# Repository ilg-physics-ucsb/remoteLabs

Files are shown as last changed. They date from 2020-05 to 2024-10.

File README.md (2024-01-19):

# UCSB Physics Remote Labs
This is the code base for remote-controlling apparatus used for laboratory instruction in modern physics labs.  It was created to serve our students who can't come onto campus during quarantine 2020.

## Installation and Setup

At the time of writing we are using the Raspbery Pi 4 (4GB model) with Raspbian Lite Buster installed. Raspbian Lite was chosen to minimize overhead on the CPU while still using a distro design for use with UV4L.

### Raspbian Lite

The simplest way to get Raspbian Lite is to go to the [Raspberry Pi downloads](https://www.raspberrypi.org/downloads/) page and follow one of the first three links to download the imager. Choose the link based on the operating system you are running on your own computer, not the Raspberry Pi.

Once you have the imager installed simply ask it to flash Raspbian Lite onto the SD Card. You do this by clicking the select OS button and then selection other Raspbian OS's. Then select Raspbian Lite 32-Bit. 

---
#### Making SSH work

Before you put the SD card in the Pi, you will need put an empty file named ssh in the root directory of the sd card. You can do this is terminal/command prompt.

In terminal `cd` to the SD card. On OSX that is usually under /Volumes/boot. On Linux I think it is in /mnt/boot (but I don't know for sure), then run the command

```bash
sudo touch ssh
```

On Windows open a command prompt and type `<letter>:` Replace <letter> by whatever capiatl letter windows assigned to the SD Card. (Typically D or E). Then run the command

```
echo "" > ssh
```

#### Making WiFi work

You are almost ready to plug in the SD Card.  The final step is to enable ``headless'' operation of the Pi (i.e., without its own keyboard/mouse/monitor) by giving the Pi access to your WiFi when it boots. To do that you need to add one more file to the root directory of the SD card.  This file must be named [wpa_supplicant.conf](https://www.raspberrypi.org/documentation/configuration/wireless/headless.md) 

On Windows, you can make the file in any simple text editor on your computer and then drag and drop it onto the SD card. On Mac, there can be issues when copying and pasting to a text editor and then moving it. It is best to type it out long form. The contents of the file should look like the following:
```bash
ctrl_interface=DIR=/var/run/wpa_supplicant GROUP=netdev
update_config=1
country=<Insert 2 letter ISO 3166-1 country code here>

network={
 ssid="<Name of your WiFi>"
 psk="<Password for your WiFi>"
}
```
Replacing the three entries between angle brackets < > with your information.

Now you can plug in your SD card into the Pi and boot. You should then be able to SSH into your Pi.

---
### SSH

#### Getting the IP Address
In order to connect to your Raspberry Pi, you will need to know its IP Address. To figure that out, typically log onto your router and look and the DHCP leases. How to do this varies from router to router, but it typically starts by opening a browser and typing "192.168.1.1" in the adress bar (without the quotes). If that doesn't work try "192.168.0.1" and if that doesn't work try "10.0.0.1". If none of those work try the following commands in terminal/command prompt/Powershell:

OSX/Linux
```bash
ifconfig
```

Windows
```
ipconfig \all
```
And look for somthing labeled "gateway" that should be the IP address of your router. Type that set of numbers into your browser's address bar.

Finally, if that doesn't work, google the make and model of your router.

To access your router's information typically requires a username and password. Most routers have a default that is written on the bottom of the router or available via google. If you haven't changed anything then that should be the log in information.

You will have to look around your router's website to find a list of connected devices and their IP addresses. One of them should be named "raspberrypi". Again it should look like 192.168.1.61 or something similar. (Note: you want the IPV4 address not the IPV6.)

---
#### Getting into the Pi

To SSH into your Pi use Terminal or Powershell *(not command prompt)*. Simply type the command

```bash
ssh pi@<ip_address>
```

Replacing <ip_address> with the address you found one your router's website. (Note: Make sure your Pi has been on for about a minute before you try this command.  It won't work if the Pi is still booting up.)

You will be asked for a password. The default password for raspberry pi's is the word "raspberry" without the quotes.

The terminal should then look somthing like 
```
pi@raspberrypi:~$
```
If everything went seccussfully.

---
### Configuring the Pi
Now run the command
```bash
sudo raspi-config
```
This will open a colorful window that you can navigate using the tab, enter and arrow keys.

Start by changing your password to something that you will remember. (Just press Enter on your keyboard.)

Then arrow down to "5 Interfacing Options"

You will want to do a few things in that window, but be aware that each time you make a selection it kicks you back out to the main screen and you have to go back to "5 Interfacing Options".

- Make sure the SSH is enabled.
- Then enable Remote GPIO
- Next enable the Camera
- Then enable I2C

You may want to change the Hostname of the raspberry pi so that you can identify it more easily. To do that, select "Networking" from the raspi-config page and change the hostname. It will show you a list of rules the hostname must follow. You will have to reboot the raspberry pi in order for the name change to take effect.

Finally arrow down to "8 Update" and hit Enter. 

---
### Adding I2C Bus
Many of our labs are using the Arducam Raspberry Pi Multi Camera Adapter Module V2.2 and the Adafruit DC & Stepper Motor HAT for Raspberry Pi - Mini Kit. The problem with using both of those kits is that both use I2C and have a hardware address of 0x70. Thus they conflict. To solve this we need to configure an additional I2C bus on the GPIO headers. At the time of writing (July 2020) there is an [issue](https://github.com/raspberrypi/firmware/issues/1401) with the firmware that comes on the Raspberry Pi 4B preventing us from doing this. So before you can add the code you need to run the command.

```bash
sudo rpi-update
```
This will update the firmware to solve the boot issue. Then you need to do the following

```bash
sudo nano /boot/config.txt
```

Go down to an area referencing Additional Overlays (however it can be anywhere in the file) and the the following line:

```
dtoverlay=i2c-gpio,bus=11
```

This will create a new I2C bus out of physical pins 16 & 18 (BCM 23 & 24) where 23=SDA and 24=SCL lines. For us this made it on bus 11. You can specify other pins or which bus number to use if you would like. To do this look at the /boot/overlays/README file. Ctrl-F "i2c-gpio" for instructions. You now need to reboot for changes to take effect.

```bash
sudo reboot
```

**If something should go wrong:** If you can't boot then you need take out the SD card and look at the config.txt file on another computer. You can comment out the line you added with #. If that doesn't work either than something may have gone wrong with the rpi-update. In which case it is best just to reflash the SD Card and start again. You won't want to run rpi-update, but find the file in the issue listed above and replace it in place.

Once rebooted check which bus was added to your pi by running

```bash
ls /dev
```

Then look for something i2c-11 or i2c-3. You should already have i2c-1 by default, so if that is the only one something went wrong.

**NOTE:** In order for your new pins 16 & 18 to behave properly you will need to add a pull up resistor to each pin. That is, you will need a 1.8 kOhm resistor going from pin 16 to 3.3 V rail and another 1.8 kOhm resistor going from pin 18 to the 3.3 V rail.

---
### Installing Dependencies

The remote lab software needs some programs installed in order to run. 

Start by updating the package manager and upgrading all the elements therein by running the commands
```bash
sudo apt update
sudo apt full-upgrade
```

Once that is done, perform the UV4L ARM Installation [https://www.linux-projects.org/uv4l/installation/].

First run
```bash
curl http://www.linux-projects.org/listing/uv4l_repo/lpkey.asc | sudo apt-key add -
```
Then add a line to the ```sources.list``` file. To do this simply run:

```bash
sudo nano /etc/apt/sources.list
```
Then arrow down to the last line and copy the line below and paste it into the raspberry pi terminal.

```
deb http://www.linux-projects.org/listing/uv4l_repo/raspbian/stretch stretch main
```

Then update agian to update the list of packages, and finally run the command to install everything we need.

```bash
sudo apt update
sudo apt install uv4l uv4l-uvc uv4l-server uv4l-webrtc uv4l-raspicam uv4l-raspicam-extras python3-pip git i2c-tools
```

Once everything is done installing we will now need to install some Python Packages that are required. Run the following command.

```bash
pip3 install RPistepper pyvisa pyvisa-py adafruit-circuitpython-motorkit python-tplink-smarthome dlipower
```
---
### Getting Remote Labs files.

Now we need to get this repo onto your Pi. Just run the following command:

```bash
git clone https://github.com/ilg-physics-ucsb/remoteLabs.git
```

Then run `cd remoteLabs`

From this folder you will want to run the two commands

```bash
sudo mv uv4l-uvc.conf /etc/uv4l
sudo mv uv4l-raspicam.conf /etc/uv4l
```
---
### Running the Remote Labs

To get the controllers to run you will need to add the labcontrol directory to your PYTHONPATH. To do this first run the command:

```bash
sudo nano ~/.bashrc
```

Then add to the top of the file the following:

```
# prepend the local file containing modules to the path that PYTHON searches for imports
export PYTHONPATH="/home/pi/remoteLabs":$PYTHONPATH
```
Press Ctrl+X, then "y" then Enter/Return.

Now run the command

```bash
source ~/.bashrc
```

In order to run UV4L you need to do the following if you are using a USB camera:

```bash
sudo pkill uv4l
sudo uv4l --config-file=/etc/uv4l/uv4l-uvc.conf -d uvc --driver-config-file=/etc/uv4l/uv4l-uvc.conf --enable-server yes
```

And if you are using one of the CSI Raspicams run the following:
```bash
sudo pkill uv4l
sudo uv4l --config-file=/etc/uv4l/uv4l-raspicam.conf -d raspicam --driver-config-file=/etc/uv4l/uv4l-raspicam.conf --enable-server yes
```

Then you need to run our python controller. For example, for the photo-electric controller lab

```bash
cd ~/remoteLabs/PhotoElectricEffect
python3 photoElectricController.py
```

Now on your computer, not the Pi, point your browser to:

http://<ip_address>:5000

Where you replace <ip_address> with the Raspberry Pi's IP address.

Remote Labs Repository © 2020 by University of California, Santa Barbara, Instructional Lab Group is licensed under CC BY-NC 4.0

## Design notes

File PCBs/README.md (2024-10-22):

# Remla PCB Design Principles

This is a very general PCB prototyping tutorial for beginners. If you have designed and prototyped PCBs before and did not have much trouble with it, skip.

## Design Software

We use JLC's EasyEDA tool to design PCBs due to its beginner friendly UI and great manufacturing/prototyping integration.
We have an account for lab use only: <remotelabs@physics.ucsb.edu>

## Design Steps

### Preparation

- Identify your problem.
- Prepare a brief circuit diagram.
- Research IC/component options.
- Download EasyEDA.

### Make a PCB

- Start new EDA project.
- Add a schematic and draw out the circuit.
- **ALWAYS check the circuit before continuing.**
- Add a layout file and do some routing.
- Make sure you know your circuit's electrical charachteristics and add design rules if necessary.
- **ALWAYS run DRC as you design your layout.**

> DRC stands for Design Rule Check. It is vital that some rules are met so that certain manufacturing steps can proceed without problems. It is also important that stricter rules are followed to ensure electrical characteristics align with our design goal (e.g. wider traces for lines carring significant current, no 90 deg angles for high speed signal lines, etc.).

> Note: You must refresh the layout every time you make new changes to the circuit schematic to make sure changes are updatd in the layout file.

- Check the circuit again and make sure the layout matches your schematic and component placements do not overlap.
- If PCB assembly (PCBA) is in order, check component suppliers and serial numbers to make sure they are indeed the components you want.
- Export design files: Gerber (PCB layout), BOM (bill of materials), PickAndPlace (assembly coordinates).

> Note: BOM and PickAndPlace files are only necessary if assembly is in order.

### Save Your Progress

- Save your project (you can export the EDA's .epro project file) to the repository as well as any exported prototyping files in the last step.

### Place an Order

- Login to JLC with <remotelabs@physics.ucsb.edu>.
- Upload the exported files specified above.
- Choose manufacturing parameters. Common manufacturing parameters are the cheapest as they are produced in mass.
- Place the order and notify admin to pay for the order.
- Wait for about 2 weeks.
- Pick up the package at physics logistics warehouse in Broida.

### Testing Your PCB

**DO NOT plug in your untested circuit to a working circuit yet!**

- Check powerlines and their polarity.

> If your circuit requires external power supply or has its own voltage regulations, check if power lines are connected and if all power circuit testpoints can produce the specified voltages.

- Check connectivity in vital signal lines
- If things look good at this point, pray to the almighty god of your choice and plug in your board to a **non-production** test circuit.
- Check software compatibility on the **non-production** testbench.
- If everything functions in all modes of operation, thank your god of choice and proceed to upgrading all applicable setups with your shiny new boards.

### Production Deployment

- Shutdown the host and disconnect power safely to avoid transient bursts.
- Plug in your new board.
- **Reboot host and update accomodating software.**
- Start server process.

## When Things Go South

**Please pay extra attention in this section if you are new to electrical engineering or have not burnt a circuit before.**

If the design rules are followed, there should not be damage to the production environment or significant hazard. However, if it is the case, do not panic. **Remember that yours and everyone in the lab's safety is the top priority.**

With DRC checks and circuit diagram checks in place during the design process, it is unlikely that catastrophic failures will occur. However, remember that electrical failures can cause severe safty problems.

### Hardware Failure

An error in the hardware can be identified by **extream mechanical response, burnt smell, smoke, sparks, abnormal heat in the circuit, or the host hardware becoming irresponsive, etc..**. Avoid touching hot or buring components directly and rememeber **shorted wires become extreamly hot even if they don't look like it**!

- Disconnect all power to the setup immediately.
- Extinguish fires if there is any and remove flammmable materials from site.
- Wait for the setup to cool down.
- Examine the remains and identify points of failure.
- Check schematic and layout to identify the error in the circuit.
- Go back to fix errors and make a new PCB.

> Sometimes small hardware errors can be rectified by manually making jumper routes or disconnecting nodes by cutting the copper layer in the PCB. In this case, it may not be necessary to reorder a new PCB. However, **ALWAYS document this failure** and fix the shematics. 

### Software Failure

Software failures can be identified by **abnormal mechanical response, host software warnings and errors, host software becoming irresponsive, etc..**
Errors in the software can occationaly cascade into hardware failures! Therefore, depending on the severity, disconnect power if necessary and revise software in a different environment.

- Revise software in a safe environment or a testbench.
- Check software version.
- Check driver software compatibility.
- Make changes to your software and go back to step 1 in software failure handling.
- When error is fixed, go back to Production Deployment.

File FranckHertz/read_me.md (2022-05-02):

# Multithreading Documentation
in order to allow multithreading, we essentially need to create locks that prevent certain devices from running at the same time and queues up commands for devices that are locked.
## Add_lock Function

The add_lock function is defined in line 60 of experiment.py

This function must take in an iterable and allows multiprocessing by placing a lock on a single or multiple devices. Locking devices disables devices that share that lock from being ran at the same time. When a command is sent to a device, the device acquires the lock, disabling all other devices (including itself) executing any commands. Instead these commands are put into a queue and executed in first in first out order as soon as the original device finishes executing and releases the lock.

If two devices should not be ran at the same time, put both devices into an iterable (i.e. [device1, device2]) to create a lock that both devices share. If a device can be ran at the same time as every other device, you must still give it its own lock by placing it in an iterable (i.e. ([device1])) to enable multiprocessing and to allow multiple commands to be queued for that device.

## Changes to the codebase
### Command Thread
This thread allows us to input multiple commands to be ran in parallel. The thread is created and executed in command_handler in experiment.py. For each new command, we create a new instance, or thread, of cmd_handler in controller.py, which executes the command. This thread takes in the data decoded from data_connection (command, params, device_name) in addition to a response queue, which handles the response between the command thread and the response thread. 
### Cmd_handler
In controllers.py, cmd_handler returns a response into the queue, which is an iterable of [response, device_name].This function also handles the multithreading locking between devices. When a new instance of cmd_handler is created through the command handler, the function first acquires the lock the device is assigned to. If this lock is not available, the thread waits until the lock becomes available. In the case of multiple commands, the commands are queued up and executed in first in first out order. After the lock has been acquired, the function then executes the command. It then release the lock and inputs the response and the device_name into the queue.

### Response Thread

This function was the latter half of the command_handler function in experiment.py. This function takes in a queue as a parameter that contains the response of the Command thread. This function threaded to run on its own single thread separate from the program. The thread is ran when data_connection is called before looping to receive any data connections. 

This function logs data and updates the states of  the devices. These are race conditions, so this thread can only be ran once at a time. This function waits for a response from cmd_handler in controllers.py.  The function grabs the response and the device_name from the queue. It then logs data and updates the states of the device and then waits for the next item in the queue. 

- created by Marlon Munoz

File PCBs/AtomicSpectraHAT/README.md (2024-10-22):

# Atomic Spectra HAT

> This is a PCB design for the Atomic Spectra Setup, it is designed to be a HAT that can be installed on top of a Raspberry Pi 4.

## This PCB integrates 4 main functions

- 12V to 5V power generation and filtering for the 5V smaller stepper motors.
- Camera board routing to the RPi.
- S42C Encoded Stepper motor power filter and connector routing.
- Ambient LED power pass by switch.

## Board I/O

- 12V power (XH-A) input.
- 12V power (XH-A) pass by output.
- Standard 40 pin RPi connector (the connector itself needs to be sodered upside down with female facing towards the RPi since this board goes on top of it.)
- 2x S42C connectors (XH-6A)
- 2 pin female ambient LED pass by
- 26 pin camera board connector

## Implementation

The 12V-5V power conversion is implemented with the Texas Insturment TPS630701RNMR buck-boost converter.

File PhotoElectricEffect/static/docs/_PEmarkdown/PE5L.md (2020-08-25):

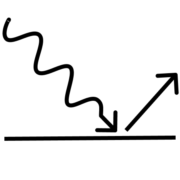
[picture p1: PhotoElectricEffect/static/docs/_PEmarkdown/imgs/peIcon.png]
icon
# The Photoelectric Effect 
---

Two critical experimental observations led to the development of Quantum Mechanics: the blackbody spectrum and the photoelectric effect. 
In this lab you will explore the photoelectric effect and use it to measure Planck's constant.

Background
---------------------

Quantum Mechanics was developed in the early 1900's, but the evidence for it began to appear even in the late 1800's. 
For example, Heinrich Hertz noticed that sparks started more rapidly when electrodes were illuminated with ultraviolet (UV) light. 
Other investigators later determined that free charges (*i.e.*, electrons) were emitted from metal electrodes illuminated by UV light. 
These were called "photoelectrons". 
Some metals, mostly the alkali metals in the first column of the periodic table, produced a steady supply of photoelectrons (called a "photocurrent") when illuminated by either UV light or visible light, but other metals only did so for UV light. 
Detailed measurements of this "photoelectric effect" established the following characteristics:

1.  For a given metal, there exists a definite cut-off frequency, $\nu_0$. 
    Incident light with frequency below $\nu_0$ produces no photocurrent regardless of its intensity.

2.  For light with frequency $\nu>\nu_0$,
    the magnitude of the photocurrent produced is directly proportional to the intensity of the incident light.

3.  The maximum kinetic energy of the photoelectrons does not depend on the intensity of the light, but it is 
    proportional to the frequency of the incident light.

These characteristics could not be explained by the classical description of light as a wave that continuously transmits energy in proportion to the intensity of the light. 
Explaining these observations required a different description for light, which was proposed in papers by Max Planck (1901) and Albert Einstein (1905).[^1]

They proposed to describe light as consisting of discrete bundles of energy, rather than as a continuous stream of energy. 
The bundles, or "quanta", of energy were named *photons*. 
Each photon carries an energy of $E=h\nu$, where $h$ is Planck's constant with units of energy times time. 
The name of this constant honors Planck because he was the first to use the idea of quanta to explain the blackbody radiation spectrum. Einstein then used it to explain the photoelectric effect as follows.

A photon of incident light transfers all of its energy to an electron in the metal. 
If that energy is sufficient, it can dislodge the electron from the metal, 
*i.e.*, it does some amount of work, $W$, to overcome the potential energy binding the electron in the metal. 
Any excess energy goes into the kinetic energy of the ejected electron,
$$
E= W +\frac{1}{2} m v^2 
$$
Using the photon energy, $E=h\nu$, we get
$$
\frac{1}{2} m v^2 =h\nu -W
$$

Not every electron in the material experiences the same potential, so the work required to eject them varies and their resulting kinetic energy varies. 
However, there is a minimum amount of work required for the most loosely bound electrons, which corresponds to a maximum kinetic energy for the ejected electrons. 
We can measure that maximum kinetic energy by applying a "stopping voltage" which the photoelectrons must overcome to be detected. 
If we call $V$ the voltage required to stop the most energetic electrons (and all the other electrons as well, of course), then $eV_s = \frac{1}{2}mv_{\rm max}^2$. Putting this all together we get the expression
$$
V_s =h\nu/e -\phi
$$
where $\phi$ is called the "work function" of the metal and corresponds to the minumum work required to eject an electron from that particular type of metal. 
Since we divided through by $e$, the work function $\phi$ has units of volts.

This equation is a straight line on a graph of $V_s(\nu)$, with a slope of $h/e$ and a $y$-intercept of $\phi$. 
By measuring $V_s$ for different frequencies of light and fitting such a line we can determine both Planck's constant and the metal's work function.

Instruments
---------------------
The apparatus used in this lab consists of
* **a mercury (Hg) discharge lamp** - which provides the light that will eject electrons from the metal.  

::: Figure:Figure
lamp
:::

Mercury is an ideal light source for this purpose because it emits a lot of light, but only in a small number of wavelengths.  Figure 2 is a plot of Mercury's emitted light intensity as a function of wavelength.  This kind of plot is called an *emission spectrum*.

::: Figure:Figure
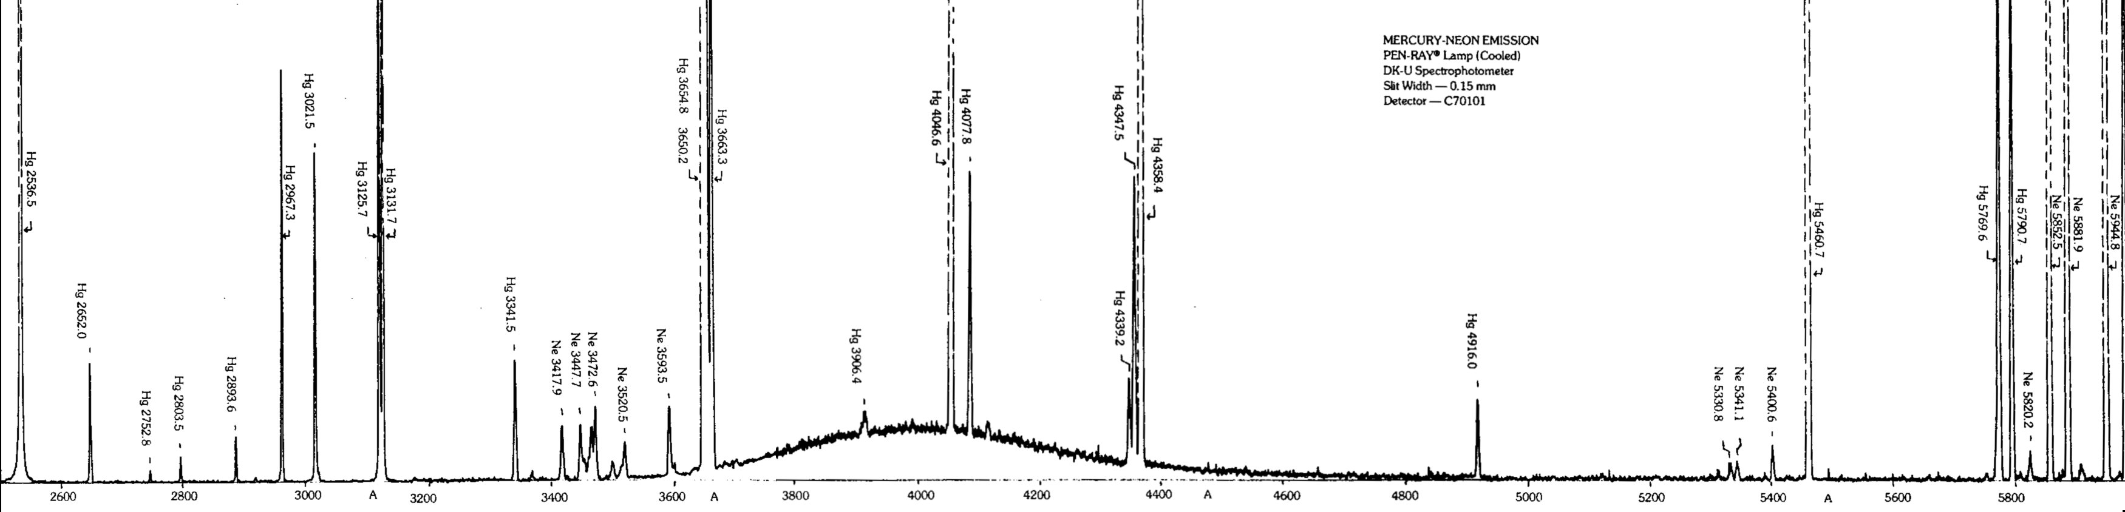
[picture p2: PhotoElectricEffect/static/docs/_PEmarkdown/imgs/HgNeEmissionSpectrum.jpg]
HgEmission

The horizontal axis is wavelength in Ångströms ( $1$Å $=10^{-10}$m),  the vertical dashed lines are the edges of peaks whose intensities are too large to plot on the vertical scale used, and the numbers labelling each peak indicate that peak's central wavelength, again in Ångströms.
:::
* **a wheel of interference filters** - each of which transmits light only in a narrow range of wavelengths, $\lambda = c/\nu$,  and blocks light of all other wavelengths.  Using different filters allows you to change the energy, $h\nu$, of the light that falls on the photocathode.

:::Figure:Figure
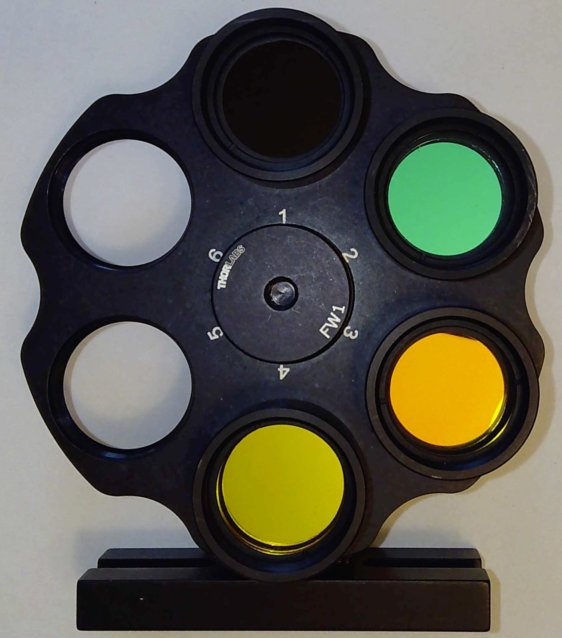
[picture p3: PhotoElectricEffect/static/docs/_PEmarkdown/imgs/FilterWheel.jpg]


 You can view these individual filters' transmission spectra on the web-portal for this experiment. 
:::

* **a phototube** - which holds two metal electrodes under vacuum.[^2]  One of the electrodes is a large, curved rectangle.  The other is a thin cylinder.  The curved rectangle is called the “photocathode” — *cathode* because it attracts cations (or positive charges) and repels (or, in this case, ejects) anions (in this case, electrons) –– and *photo* because it will only do so so when light hits it.[^3]  The photocathode’s curved shape helps concentrate the ejected electrons along the axis of curvature, which is where the thin cylinder is positioned.  The cylinder is called the anode because it is the electrode that attracts anions (*i.e.*, collects the ejected electrons). 

:::Figure:Figure
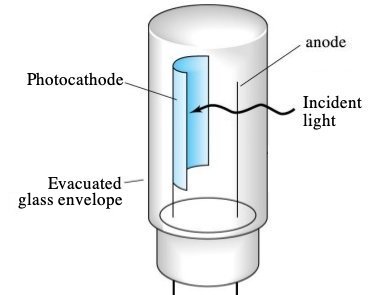
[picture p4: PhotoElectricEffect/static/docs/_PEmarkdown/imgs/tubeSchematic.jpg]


You can't see the phototube on the live feed for this experiment because it is mounted in a  box that has only a small hole to let in the light from the Hg lamp and is otherwise light-tight.

:::

:::Figure:Figure
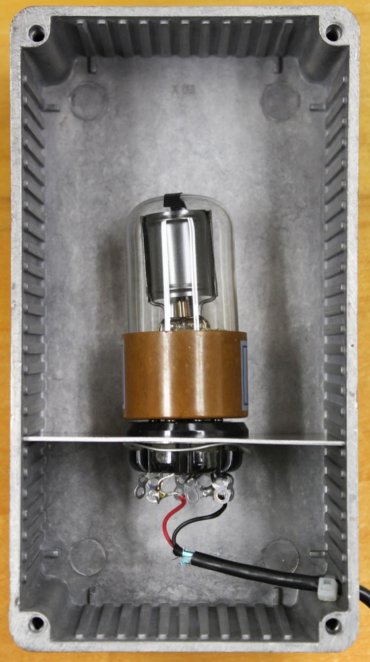
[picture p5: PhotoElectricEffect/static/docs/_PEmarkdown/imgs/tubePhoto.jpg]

:::

*  **a variable voltage circuit** - which puts an adjustable voltage across the phototube using a pair of AA batteries, connected in series, and variable resistor (also known as a *potentiometer*).

:::Figure:Figure

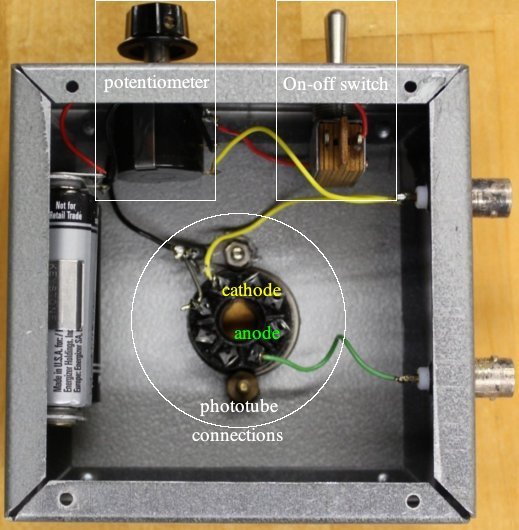
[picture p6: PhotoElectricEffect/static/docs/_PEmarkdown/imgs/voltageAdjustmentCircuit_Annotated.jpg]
potPhoto


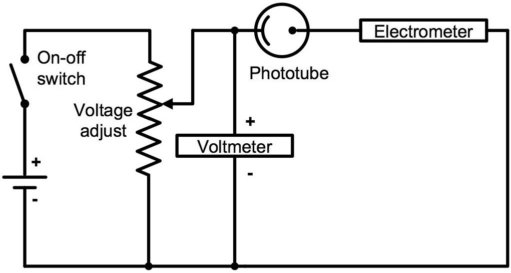
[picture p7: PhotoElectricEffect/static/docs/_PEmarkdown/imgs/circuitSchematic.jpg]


 The circuit is designed to hold the anode at a more negative potential than the photocathode.  
:::
    
* **a digital multimeter (DMM)** - which measures the potential difference between the photocathode and the anode.

:::Figure:Figure

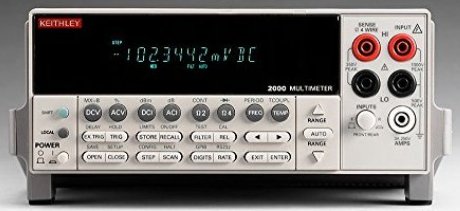
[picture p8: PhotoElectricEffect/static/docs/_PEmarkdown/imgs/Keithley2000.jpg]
Keithley 2000
 
:::

* and, last but not least, **a sensitive electrometer** - which measures the photocurrent and can reliably detect mere fractions of a picoampere (1 pA = $10^{-12}$A).

:::Figure:Figure

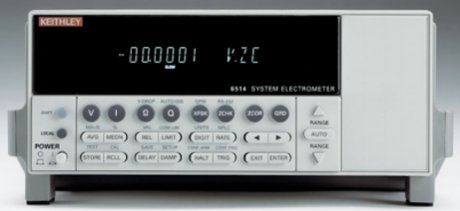
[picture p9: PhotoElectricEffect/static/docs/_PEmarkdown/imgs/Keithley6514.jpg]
Keithley 6514


Manuals for these meters are available in PDF format on the web-portal for this experiment. 
:::

Approach
---------------------
Using the instruments above, you will filter the light emitted by a Hg lamp to get photons of very well defined energy and, for a given energy of photons incident on the photocathode, measure the potential difference between the anode and the cathode that stops all photocurrent from reaching the anode (as explained towards the end of the Background section).  

The web-portal for this experiment enables you to press and turn all the same buttons and knobs as you would in person, and observe the effects of your actions through a live video feed. The video feed is displayed at the center of the portal and controls for the knobs and buttons are distributed around it, along with links to helpful information.

:::Figure:Figure

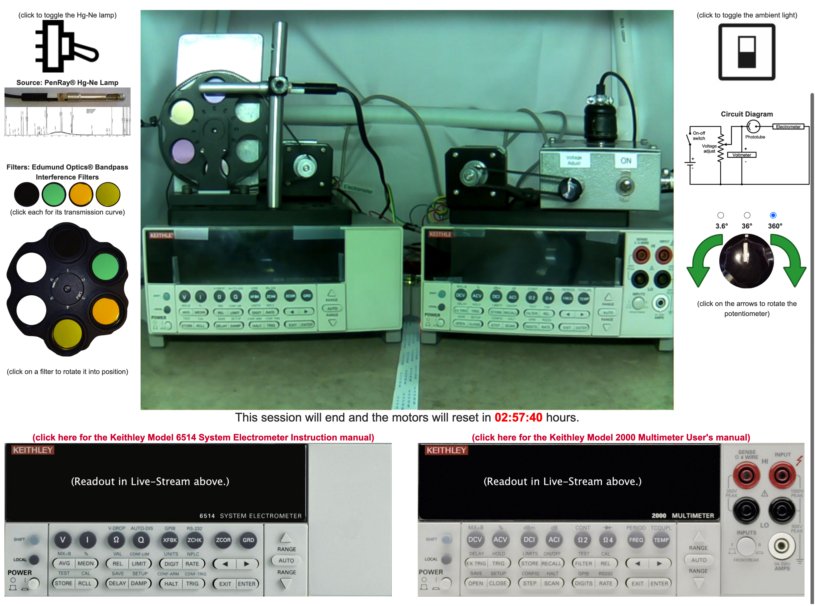
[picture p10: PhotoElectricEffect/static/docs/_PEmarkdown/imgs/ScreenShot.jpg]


Note the timer immediately below the video feed (in red).  When it runs out, the lab equipment will reset to its initial configuration.
:::

:::Exercise
### Center Video

When you first open the portal the video feed will be dark.  

* Click on the central square of the switch in the upper right to turn on the background/ambient light. 

The ambient light lets you observe the setup and better see the machinery respond to your clicks. You will want to check that it doesn't interfere with your measurements (or just switch it off while collecting data).

### Left Controls

A toggle switch in the upper left controls the power to the Hg lamp. 
* Click the image of the lamp immediately below the toggle switch to access the lamp's user manual.  
* Click the plot below that to view a high-resolution image of the lamp's emission spectrum. 
* Click the photo of a filter to view the transmission spectrum provided by its manufacturer.

::: Question
Using the emission spectrum of the lamp and the transmission spectra of the filters, determine the dominant wavelength(s) of the photons that each filter lets through.
:::

* Click the corresponding filter in the filter wheel and watch the wheel rotate to put that particular filter in between the Hg lamp and the phototube.

### Right Controls

A pair of green arrows to the right of the video feed allows you to turn the potentiometer knob clockwise or counter-clockwise.  The amount of rotation corresponding to a single click is determined by selecting one of the three radio buttons above the arrows.

::: Question
How many full rotations are required to sweep through the entire range of the potentiometer?
:::

### Bottom Controls

Along the bottom of the web-portal are images of the front panels of the electrometer (on the left) and the multimeter (on the right). 
Each image is actually a fully functioning interface to the corresponding device!  
Clicking on a button in the image will cause the device to respond exactly as if you had pressed the that button in person.

* The first thing you should do when you start to work with the apparatus is turn on the meters so that they have time to warm up. 

Most equipment has a "warm up" period, which is simply the time it takes for all the heat production and dissipation mechanisms to come to equilibrium so that the device's components remain at a constant temperature.  Variations in temperature can alter operational details of electronics, such as amplifier gains and leakage currents. The electrometer in particular has calibration circuitry that measures and corrects for most of these temperature dependent effects, but operating at a stable temperature still improves its precision. 

The Keithley 6514 electrometer is central to your measurement, so you may be curious to understand its operation. 
* Click on the red-lettered link above electrometer control panel and skim the user manual's table of contents.

You will notice that the  electrometer can be used to measure voltage, current, resistance or charge. When powered on, it defaults to voltage measurement mode.  For this lab, current measurement is the only relevant capability. 

* Switch to current mode using the front panel button.

The electrometer has ten ranges for current measurement, with the full scale
values ranging from 20 pA to 20 mA. 
:::Question
When the range is set to 20 pA full-scale, how many digits after the decimal point are displayed? 

How many electrons per second does a single unit in that smallest decimal place represent?  

(Recall that 1 Ampere = 1 Coulomb per second and 1 Coulomb $= 6.2\times10^{18}$ elementary charges)
:::

* Select an appropriate range for your measurements using the up and down arrows. 
* Set the RATE setting to SLOW 
* Set the DIGIT setting to display 2 or 3 digits after the decimal point. 

Displaying more digits provides greater precision, but temporal variations typically limit the usable level of precision.
:::

::: Exercise
The Keithley 6514 electrometer is capable of measuring very small currents with great precision, but that precision requires some careful procedures. In particular, it is helpful to calibrate and correct for any offset currents. This can be done with the Zero Check and Zero Correct functions. 

When Zero Check is enabled, the input signal is shorted so that the input amplifier sees only offset currents and voltages that are not part of the input signal and thus should be subtracted. That subtraction can, and should, be done internally using the Zero Correct function, following the procedure below. 

### Zero Correction procedure to remove offsets

1.  If you haven't already, select the current measuring mode by pressing I. 

2.  Select an appropriate measurement range.

3.  Press ZCHK to enable Zero Check mode. You should see a "ZC" message
    appear to the right of the units on the display.

4.  Press ZCOR to subtract the reading in Zero Check mode from future readings. You should see a "ZZ" message appear in the display.

5.  Finally, press ZCHK a second time to disable the Zero Check mode.
    You should see a "CZ" message appear in the display to indicate that the  readings are being corrected for any zero point offsets.

6.  If you ever want to abandon the Zero Correct mode, for example, if you want to check with it is dramatically affecting your measurement, just press ZCOR a second time.

It is *reasonable* to perform the zero correction procedure between each set of measurements ( *e.g.*, for each new filter) to compensate for any drifts that may occur over time.

It is * **essential** * to repeat the zero correction procedure before making a measurement on a more sensitive scale than the last. The offset currents in the machine depend on the measurement scale.  If you correct the offsets at a less sensitive scale and then move to a more sensitive scale without repeating the zero correction procedure, the readings on the more sensitive scale will likley be incorrect because too large of an offest is being subtracted.
:::

Measurement
-----------

There are four optical filters which only pass light in a narrow range of frequency. 
By placing these different filters between the Hg lamp and the phototube (see Exercise 1, Left Controls), you can measure the phototube's response as a function of the light's frequency, $\nu$. 

:::Exercise

With a filter in place, adjust the impeding voltage, $V$, until the photocurrent, $I$, reaches zero; 
the impeding voltage that stops all the current is the stopping voltage $V_s$. 
To make a more precise measurement of $V_s$, you could measure $I$ as a function of $V$ and fit the data to obtain $V_s$. 
* Take a quick, coarse scan to get an idea of the overall shape of $I(V)$. 

:::Question
Which filter did you choose?  
:::

:::Question
What is the overall shape of I(V)? 

Answer in words only.  Use adjectives like {positive, negative, increasing, decreasing, linear, non-linear},  verbs like {approaches, crosses, saturates} and adverbs like {near, far, above, below, at}.
:::

* Decide on a set of voltages that seem appropriate for the filter you chose and record a table of $I(V)$ measurements.

:::Question
What is $V_s$ for the filter you chose?
:::
:::

:::Exercise
* Repeat Exercise 3, answering all of the questions therein, for each of the remaining three filters.  
* Make sure to use the same method for determining $V_s$ for every filter.
:::Question
How did you determine $V_s$?
:::
:::

:::Exercise
* Plot $V_s(\nu)$. $\Rightarrow$**Make this the well-formatted plot you submit for grading. **$\Leftarrow$
* Fit your data to the equation 
$$
V_s =h\nu/e -\phi
$$
to obtain Planck's constant, $h$, and the work function, $\phi$, of the CsSb alloy. 
:::Question
What value did you use for $e$?
:::
The currently accepted value of Planck's constant is $h=(6.62606957 \pm 0.00000029)\times 10^{-34}~\mathrm{J s}$. [^3]
:::Question
How large a fraction of the accepted value is the discrepancy between your measurement of Planck's constant and the accepted value?

Calculate this *proportionate discrepancy* by taking the difference and dividing it by the accepted value:
$$
\frac{|h_\mathrm{measured}-h_\mathrm{accepted}|}{h_\mathrm{accepted}}\,.
$$
Give your answer as a percentage.
:::
:::
<hr>
(Click )
[^1]: The quantum explanation for the photoelectric effect is described concisely in a three page section of Einstein's paper, Ann. Physik 17, 132 (1905), and was the reason for his subsequently being awarded the Nobel Prize.

[^2]: Removing gas particles from the space between the electrodes greatly reduces the chances that ejected electrons will collide with anything on their way from the cathode to the anode. The vacuum isn’t perfect, of course, but it is good enough that some of the ejected electrons have a good chance of reaching the anode without losing any energy...which is crucial for measuring the maximum kinetic energy of the ejected electrons.

[^3]: The photocathode's inner surface is coated with a special alloy of Cesium (Cs) and Antimony (Sb) metals that has electrons which are not very tightly bound, and so can be ejected by relatively low-energy (*i.e.*, visible) photons.

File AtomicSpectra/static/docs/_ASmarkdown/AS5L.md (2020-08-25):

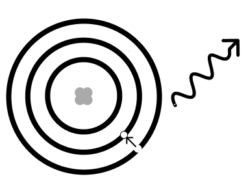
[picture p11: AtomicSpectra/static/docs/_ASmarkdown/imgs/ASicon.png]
icon
# Atomic Spectra 
---

In this lab you will observe the visible spectrum of Hydrogen and use it to measure the Rydberg constant. 
Then you will use the spectrum of two unknown sources to determine their atomic content.

Background
---------------------

The quantum explanation for atomic structure was developed in the early 1900’s based largely on measurements of the wavelengths of light emitted by atoms in [gas-discharge lamps](https://en.wikipedia.org/wiki/Gas-discharge_lamp).  
These measurements, first made in the late 1800’s, provided evidence that the energy levels of atoms are quantized (*i.e.* have a discrete set of possible values).
In particular, in 1885, Johann Balmer measured the visible spectrum of Hydrogen and found the wavelengths of light that were present were related according to

:::Figure:Equation
$$
\frac{1}{\lambda} = R\left(\frac{1}{2^2}-\frac{1}{n^2}\right); \,\,\,\mathrm{for}\,\,n>2.
$$
:::
The ultraviolet and infrared portions of the Hydrogen spectrum were later measured (by Lyman, Paschen, Brackett and Pfund) and found to fit similar formulas but with integers other than 2 in the first term (and in the inequality). They all measured the same coefficient, $R$, called the Rydberg constant. 

The origin of this formula was eventually understood within the Bohr model of the atom, which posited that the light from Hydrogen consists of photons of energy $E = h\nu = hc/\lambda$ that are emitted by atoms transitioning between electronic states that have discrete energies of $E_n = -hcR/n^2$, where $c$ is the speed of light, $h$ is Planck's constant, $R$ is the Rydberg constant and $n$ is a positive integer (Fig. 1). Transitions from excited states to the $n = 2$ state produce visible light (red to violet, left to right for the four lines shown) that you will observe in this lab. Transitions to the $n = 1$ state produce ultraviolet light, and those to the $n = 3$ state produce infrared light, neither of which can be seen by eye.

:::Figure:Figure
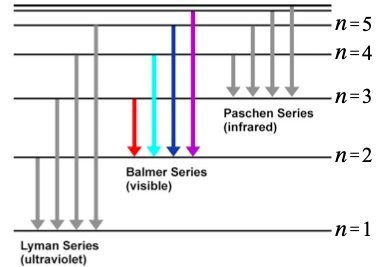
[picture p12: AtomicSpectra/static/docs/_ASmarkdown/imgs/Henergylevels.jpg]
levels


Diagram of the energy levels for a Hydrogen atom. 
:::
 This understanding allowed the Rydberg constant to be formulated in terms of purely fundamental constants like the mass, $m$, and charge, $e$, of the electron and the permittivity of free space, $\epsilon_0$:
 $$
 R = me^4/8\epsilon_0h^3c\,,
 $$
 whereas previously it had been only an empirically determined value.[^1]
 
In this lab, you will measure the visible spectrum of Hydrogen as Balmer originally did and, from it, obtain a measurement of the Rydberg constant.

Note that the Rydberg constant applies only to Hydrogen. Other atoms have a similar $1/n^2$ structure to the equation that describes their spectra, but with a different coefficient. Each element’s spectrum is uniquely characteristic, so spectra are often used to identify the elemental composition of a sample (or a star![^2]). 

After you completing your measurements of the Hydrogen spectra, you will measure the visible spectra of two unknown samples and use them to identify each sample's elemental composition.

Instruments
---------------------
The apparatus used in this lab consists of
* **a spectrum tube** -  a special kind of gas-discharge lamp that shapes the light emitted by a gas to optimally illuminate a narrow slit

:::Figure:Figure
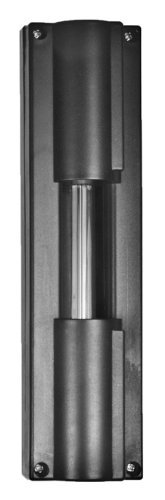
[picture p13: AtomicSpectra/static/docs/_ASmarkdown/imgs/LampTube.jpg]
lamp

:::

* **a carousel** - that rotates to power your choice of three spectrum tubes.  One contains Hydrogen gas and the other two contain gases you will identify based on their spectra. 

:::Figure:Figure
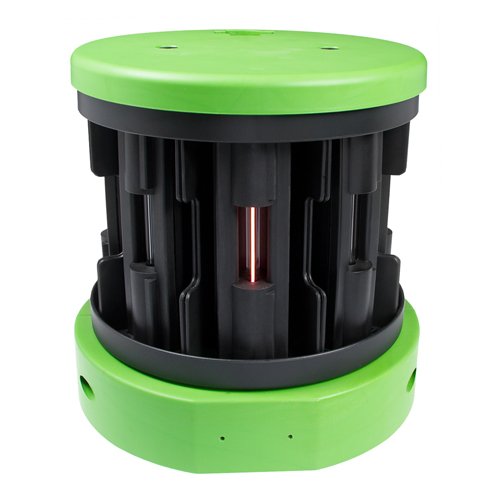
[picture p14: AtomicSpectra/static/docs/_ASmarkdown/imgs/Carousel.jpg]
carousel


You can see a top-down view of the carousel at the very right of the "overview" live feed, but the view is complicated and obstructed by various 3D-printed parts that help position and motorize the apparatus.  A mirror just to the right of center near the top of the "overview" feed reflects a sideview that clear shows when a lamp is on, off and/or rotating into position.
:::

* **a diffraction grating** - an optical element that uses the phenomenon of interference to send light of different wavelengths in different directions.

:::Figure:Figure
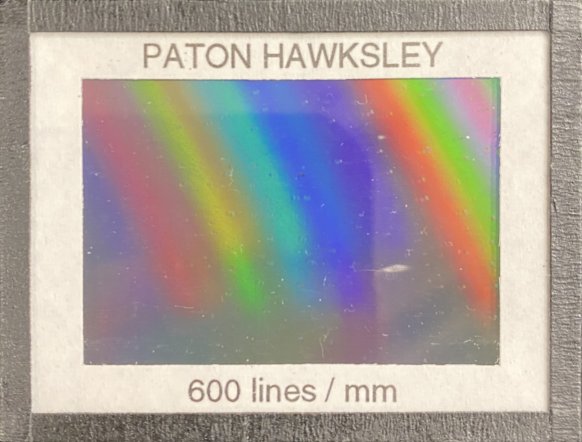
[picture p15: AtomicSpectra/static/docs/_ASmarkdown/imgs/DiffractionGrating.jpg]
grating

:::

You have learned about interference in the context of collimated light passing through a double slit.  In another lab in this course, you may have experimented with passing light through an array of three, four or five slits.  When collimated light passes through multiple, equally spaced slits, the result is an intensity pattern with maxima and minima at the same positions as in the pattern created by two slits with the same spacing, but with maxima that are much more narrowly peaked, (*i.e.*, the contrast is much improved). 

The diffraction grating you will use was made from an etching of thin parallel lines on a piece of glass. Etched regions scatter light instead of transmitting it, so the non-etched regions between the etched lines act as slits. The etching process allows hundreds or thousands of lines per mm, so this type of diffraction grating has slits that are not only plentiful, but closely spaced as well. 

Because of its very large number of slits, the diffraction grating creates very sharp maxima.  Because of their close spacing, the slits impose a large "lever arm" on the pattern (*i.e.* a greater angular separation between maxima) making it possible to distinguish maxima of subtly different wavelengths.  This can be seen from the equation for constructive interference.  Light passing through slits separated by a distance $d$ will have intensity maxima at angles $\theta_m$ for which 
$$
d \sin \theta_m = m\lambda\,,
$$
where $m$ is any positive integer. The smaller $d$ is, the larger $\theta_m$ will be for the same $\lambda$.

The $m = 0$ case is the central maximum. By measuring $\theta_m$ for $m = 1$ maxima for each of the different wavelengths, you can precisely determine those wavelengths.[^3]  

Note that this equation applies only if the collimated light is "normally incident" on the grating. You may have to adjust the grating to make this be the case.[^4] 

:::Question
What is the spacing $d$ for the diffraction grating?  (Hint: See Figure 4.)
:::

* **a spectroscope** -  which sends collimated light onto the diffraction grating and enables you to measure the various angles at which the light that passes through the grating constructively interferes.

:::Figure:Figure
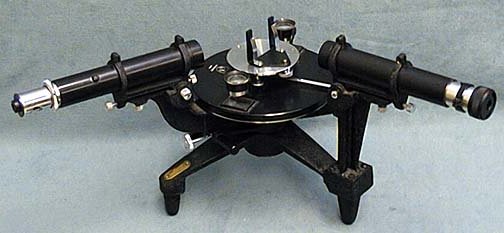
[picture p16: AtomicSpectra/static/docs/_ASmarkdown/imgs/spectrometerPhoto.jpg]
spectroscope


A manual for the spectropscope is available in PDF format on the web-portal for this experiment. 
:::

:::Figure:Figure
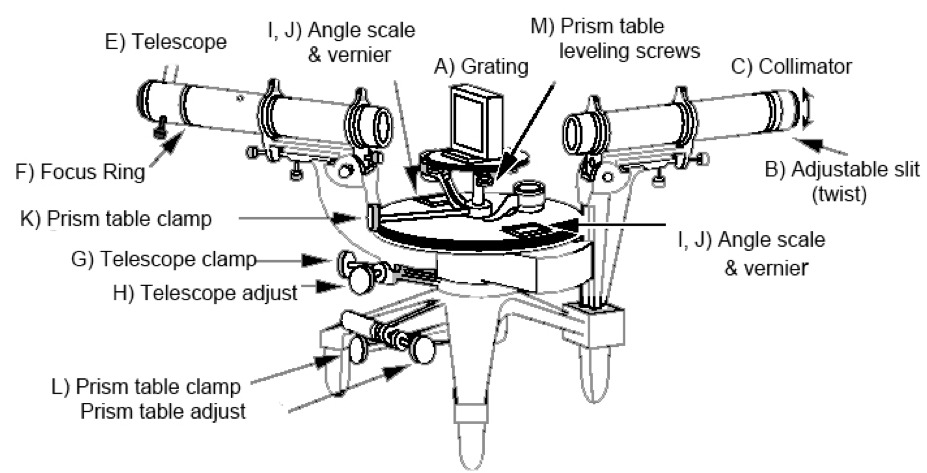
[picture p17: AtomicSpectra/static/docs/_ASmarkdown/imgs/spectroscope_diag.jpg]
spectroscopeDiagram


The parts of the spectroscope are more easily distinguished in a diagram.  
(Note that this diagram's vantage point is rotated slightly (~45° CCW) from that in the photo: the arms that are angled toward the viewer in the photo are angled away from the viewer in the diagram.)
:::

Two cylinders define the light path: the collimator (C); and the telescope (E). The collimator has an opening at its far end that only admits light through a vertical slit (B). The width of the slit is narrow but adjustable. It shapes the light beam into a vertical line. Letting the light spread vertically doesn’t degrade the resolution in $\theta$ because $\theta$ is an angle in the horizontal plane. Because a line allows more light to hit the detector, it is much easier to determine the location of a line than a point. The use of vertical slits in spectral measurements is so common that the observed maxima are called *spectral lines*.

The telescope swings to different angles around the grating (A) and images the light that comes through the grating onto a detector.  The lens at the far end of the telescope is called an "eyepiece".  If this were an in person lab, you would look through the eyepiece and your eye would be the detector.  To allow you to view the lines remotely, we have put a webcam behind the eyepiece and made what it sees available to you by clickling on the "eyepiece" button.

The angular position of the telescope is read off of scales (I,J) situated on either side of the spectrometer. The scales measure degrees down to one arc minute with Vernier markings. 
 
Using a Vernier scale takes a bit of explanation and some practice. There are some good extended descriptions online (*e.g.* [in Wikipedia](https://en.wikipedia.org/wiki/Vernier_scale)), so here we’ll introduce it with a few examples specific to the scales you will be using. The scales on the spectroscope consist two sets of uniformly spaced lines that are arranged so that they slide past each other. The lower set's lines mark each half degree, while the upper one's (which are very slightly more closely spaced) have markings corresponding to 0-30 arc minutes. The two scales are used together. 

:::Figure:Figure
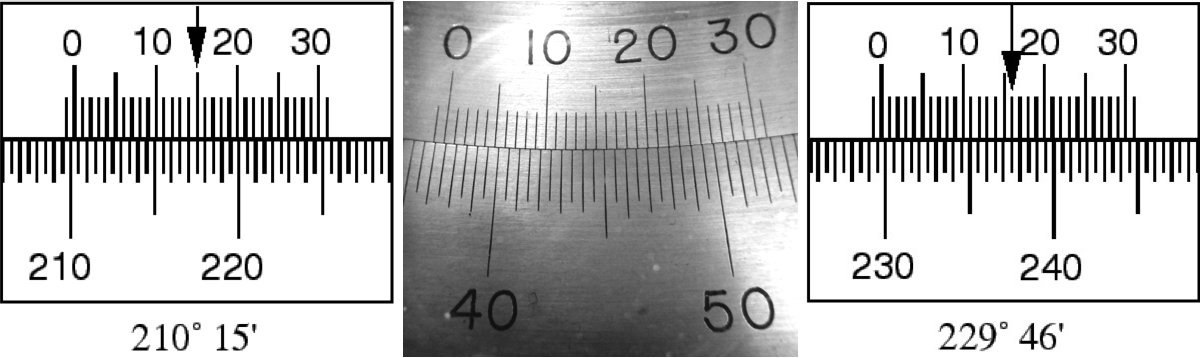
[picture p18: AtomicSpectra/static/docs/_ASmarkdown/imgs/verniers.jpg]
vernierLeft

:::
Cartoons of two different measurements are shown in Figure 7 to illustrate the procedure. First you look where the zero mark on the inner scale is located. In the left hand cartoon that is to the right of $210^\circ$; in the right hand cartoon it is to the right of $229.5^\circ$. Then you look where the lines on the inner and outer scales align most closely. In the left hand cartoon that happens for the $15^\prime$ mark; on the right side it happens at the $16^\prime$ mark. These measure the number of arc minutes to add to the values obtained from the first step. So, the measurement on the left side is $210^\circ + 15^\prime = 210^\circ + (15/60)^\circ = 210.250^\circ$, and the measurement on the right is $229.5^\circ + 16^\prime = 229.5^\circ + (16/60)^\circ = 229.767^\circ$. 

:::Question
What is the angular position indicated by the vernier scales in the photo in the middle of Figure 7? 
:::

The precision of these $\theta$ readings is limited by the one arc minute granularity of the Vernier scale, but it is possible to make mistakes in reading or calculating the values. Here are a few things you can do to reduce the chance of such mistakes and their impact:
1. Have someone else (*e.g.* your lab partner) make the same reading (without telling them what you got) and compare. 
2. Recall that the position of the telescope can be read off of scales situated on either side of the spectrometer. The angles recorded by the two scales should differ by exactly $180^\circ$. Read and record both. If, after correcting for the $180^\circ$ difference, you find that their values differ by more than the $0.005^\circ$ precision of the scales, something is wrong - if not with your readings, then with the spectrometer itself (*e.g., warping of the scales). This approach of making multiple, independent measurements of the same quantity is always a good idea and helps validate your results.
3. Record your raw readings in degrees and arc minutes, and then calculate the corresponding decimal degree values. This will help you disentangle any calculation errors that may occur. While the calculations in this case are not complicated, and the consequences of a mistake are small, this sort of fastidious data recording is a good habit to develop for professional laboratory work, when both the chances and consequences of mistakes increase.

Finally, be aware that the Verniers read angular position but the location of $0^\circ$ is arbitrary. 

In order to determine the wavelength using $d\sin\theta = \lambda$, where $\theta$ is the angle between maxima, you need to measure two angles and subtract, just like measuring a length requires two position measurements. You could do this by measuring the angular position of the central maximum, which we can call $\theta_0$ , and the angular position of the $m = +1$ maximum, which we can call $\theta_{+1}$. Then $\lambda = d\sin(\theta_{+1}-\theta_0)$. Similarly, you could measure the angular position of the $m = +2$ maximum and use $2\lambda = d \sin (\theta_{+2}-\theta_0)$ or $\lambda = d \sin (\theta_{+2}-\theta_{+1})$. Finally, note that the direction in which the angles increase or decrease on the scale is arbitrary, so you should use the absolute value of the differences.

Approach
---------------------
Using the instruments above, you will determine the wavelengths of light emitted by three different gasses.

The web-portal for this experiment enables you to manipulate the spectroscope, see the lines and read the verniers just as you would in person.  

:::Figure:Figure

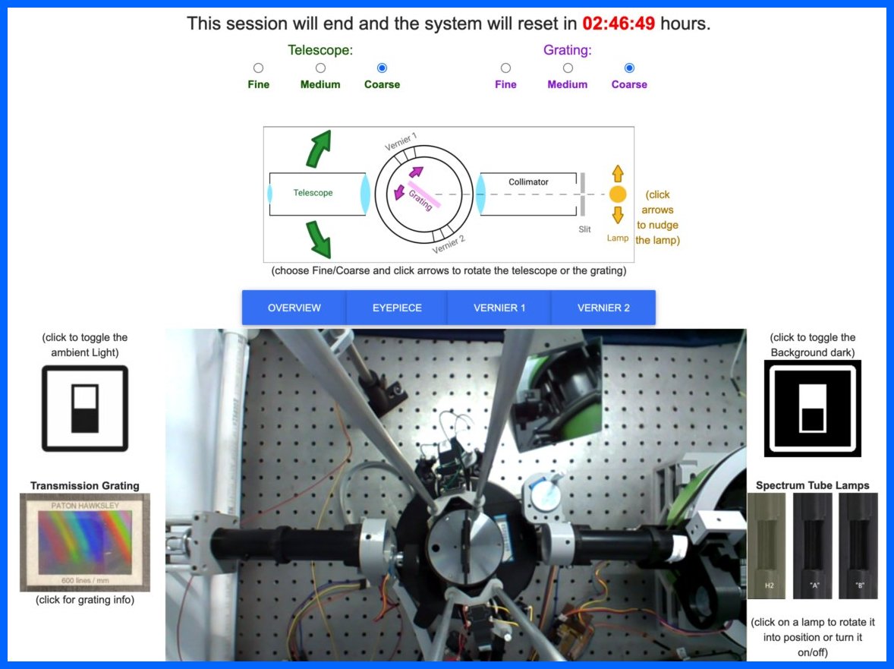
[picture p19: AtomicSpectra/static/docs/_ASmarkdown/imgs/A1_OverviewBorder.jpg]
Overview


Note the timer at the top of the portal (in red).  When it runs out, the lab equipment will reset to its initial configuration.
:::

:::Exercise

When you first open the portal the video feed will be dark.  A row of blue buttons immediately above the video feed lets you select among four cameras. 
OVERVIEW gives a top-down view of the apparatus, centered on the diffraction grating; 
EYEPIECE shows the view through the eyepiece; 
VERNIER1 and VERNIER2 each look at one of the two Vernier scales. 

* Click on OVERVIEW, then click on the central square of the white switch to the *left* of the video display to turn on the ambient light. 

The ambient light lets you observe the setup and better see the machinery respond to your clicks. 

* Click on EYEPIECE.

Ambient light reflecting off of the diffraction grating lights up the circular field of view of the eyepiece. It can't be confused for the vertical lines of light from the lamp, but it can make it hard for you to see very dim lines, so you should consider turning off the ambient light when taking your data.

* Click on one of the two VERNIER buttons and read the angular position of the telescope.

:::Question
What is the angular position of the telescope?
:::

Above the camera control buttons is a schematic of the spectrometer.  Green, pink and yellow arrows in the schematic enable you to move the telescope, grating and lamp, respectively. Correspondingly colored radio buttons allow you to change the amount moved per click. 

* Use the green arrows and radio buttons to move the telescope until the VERNIER reading is within 1° of 45° or 225°, whichever is closer to your starting point.

:::Question
What is the angular position of the telescope now? 
:::

:::Question
Describe what you did to get it there.
:::
* Switch back to the OVERVIEW camera and look at the orientation of the grating.  

The collimator and the telescope should be co-linear.  

* Use the pink arrows and radio buttons to rotate the grating until it is perpendicular to the collimator.[^4]

* Click on the image of the "H2" spectral lamp to the right of the video display.

:::Question
What color is the light from the H2 lamp?
:::

* After the lamp turns on, switch to the EYEPIECE camera. 

You should see the illuminated slit near the center of the field of view.

* Click the yellow arrows in the schematic to nudge the lamp and maximize the intensity of the light coming through the slit.

Notice that two new controls appear when you select the Eyepiece view.  
:::Figure:Figure
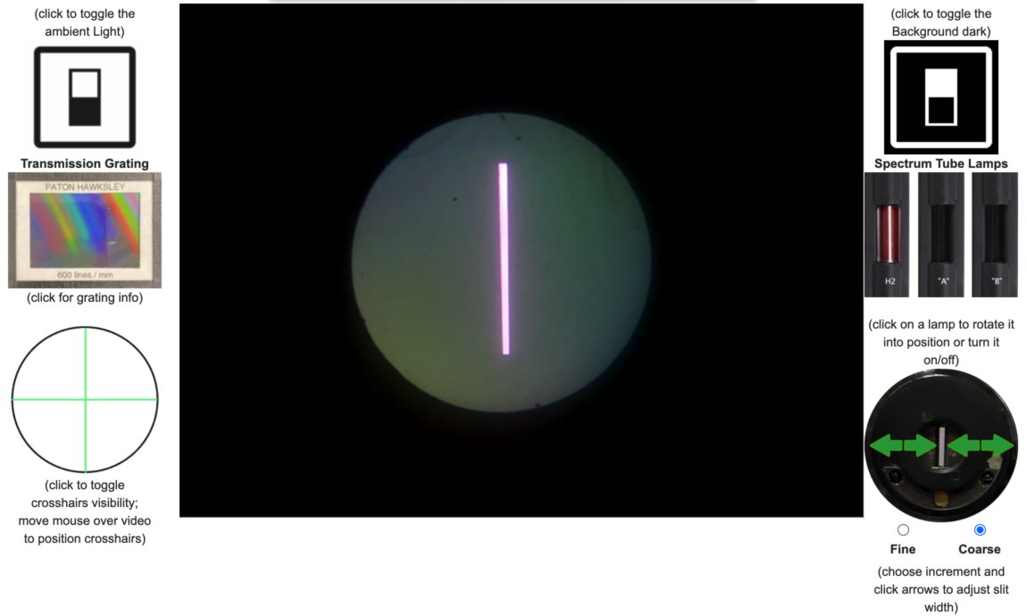
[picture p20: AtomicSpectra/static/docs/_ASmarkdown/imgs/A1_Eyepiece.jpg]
Eyepiece

:::

On the left is a button that lets you position a set of crosshairs over the live feed.  
* Click the button to activate the crosshairs, then move your cursor over the live feed to see them following your cursor.
* Click to lock the crosshairs in place.  
* Click again to release and have them follow your cursor again.  
The coordinates of the center of the crosshairs are displayed in the upper left corner of the live feed.

On the right is a photo of the slit with green arrows that let you change its width among three settings.  

:::Question
How many pixels wide is the slit in each setting? (Hint: use the crosshairs.)
::::

* Adjust the slit to its narrowest setting.
* Turn off the ambient light.
* Click on the central square of the black switch to the *right* of the video display to toggle the portal's background from white to black and back again.

Keep in mind that this can be helpful when viewing very dim lines.  
:::

Measurement
-----------
Now that you have familiarized yourself with the spectroscope and have it aligned on the central maximum, you are ready to measure the Hydrogen spectrum!

:::Exercise
### Data Collection

* Select the green radio button for coarse movement of the telescope.
* Look for the four hydrogen emission lines by moving the telescope in one direction. 

:::Question
In which direction did you move the telescope?
:::

:::Question
Which color line appears closest, and which appears furthest, from the central maximum?  
:::

Note that the violet line is the dimmest of the four and can be difficult to see. You can increase the slit width to make the lines easier to see, but you will want to balance the need for visibility with the desire for narrow lines that can be measured more precisely. 

* Move the telescope back until the central maximum is in view.
* Look for the four emission lines by moving the telescope in the other direction. 

:::Question
How do the intensities of the lines in this direction compare with the ones you saw in the other direction?
:::

Diffraction gratings are often designed to concentrate most of the diffracted energy in a particular maximum for a given wavelength. This is done by shaping, or "blazing" the grooves to have a triangular profile.  The grating in this apparatus is blazed for an $m=+1$ maximum of a visible wavelength, which is why the lines are much brighter on one side of the central maximum compared to the other.

* Move the telescope back until the central maximum is centered in the EYEPIECE view.

:::Question
What is the horizontal position of the central maximum in the live feed? (Hint: use the crosshairs.)
:::

:::Question
What is the angular position of the telescope?  Remember to record the readings from both VERNIER1 and VERNIER2.
:::

* Move the telescope in the direction of the brighter lines. 
* One at a time, bring each line to the same horizontal position the central maximum was previously at (as indicated by the crosshairs).

:::Question
What are the colors and angular positions of each of the four $m=1$ lines? Remember to record the readings from both VERNIER1 and VERNIER2.
:::

:::Question
Can you see any of the $m=2$ lines?  Note the angular position and color of any you can see. Remember to record the readings from both VERNIER1 and VERNIER2.
:::

* Move the telescope back in the other direction and and find the $m=-1$ lines.

:::Question
What are the colors and angular positions of the $m=-1$ lines that you can see?  Remember to record the readings from both VERNIER1 and VERNIER2.
:::
::::

You may see a background of colors in addition to the main bright lines. This background is typically due to the ultraviolet light emitted by the hydrogen lamp exciting other atoms to emit. In fact, that is how fluorescent lights work. Ultraviolet emission produced by running a current through the gas in a long tube excites atoms in the white fluorescent material that coats the inside of the tube. That material then emits a large number of different wavelengths that we perceive as white light. 

::: Exercise
### Data Analysis
In a spreadsheet, calculate the $\theta_m$ values of the various lines from the angular positions you measured. 

:::Question
Which angular positions did you subtract for each value of $\theta_m$?
:::

Using the $\theta_m$ values you calculated and the condition for constructive interference (given in the diffraction grating section above), calculate the wavelengths of each of the Balmer lines.

:::Question
What is the wavelength you measured for the $n=3$ Balmer line?  
:::

:::Question
What are the wavelengths you measured for the $n={4,5,6}$ Balmer lines?  
:::

Look at Equation 1 above.  

:::Question
To make a plot of your data that will let you fit a straight line whose slope will be the Rybderg constant, $R$, what should you plot on the $y$-axis?  What should you plot on the $x$-axis?
:::

$\Rightarrow$**Make this the well-formatted plot you submit for grading. **$\Leftarrow$

:::Question
What is the value of the Rydberg constant indicated by your data? 
:::

The currently accepted value of the Rydberg constant is $R=0.0109678~\mathrm{nm}^{-1}$.[^5]

:::Question
How large a fraction of the accepted value is the discrepancy between your measurement of the Rydberg constant and the accepted value?

Calculate this *proportionate discrepancy* by taking the difference and dividing it by the accepted value:
$$
\frac{|R_\mathrm{measured}-R_\mathrm{accepted}|}{R_\mathrm{accepted}}\,.
$$
Give your answer as a percentage.
:::
:::

:::Exercise
### Identify the unknowns
There are two other spectral lamps in the carousel, labeled "A" and "B".  They are each filled with one of the Noble gases.  At the bottom of the web-portal are two copies of the following image naming the five noble gases:

:::Figure
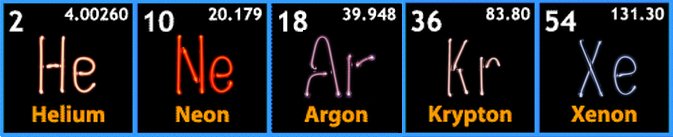
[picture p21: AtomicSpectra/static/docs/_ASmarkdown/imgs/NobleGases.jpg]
Noble Gases

:::
Click on one of the boxes naming an element to see its detailed spectrum and on the other to see the wavelengths and relative intensities of its major peaks.

* Click on one of the lamps.
* Use the spectrometer to determine the $\theta_1$ values for four of the brightest lines from this lamp.
* Use the condition for constructive interference to calculate their wavelengths.

:::Question
Which lamp did you choose?
:::
:::Question
In order of brightness, starting with the brightest, what are the $\theta_1$ values of those four lines?  What are their wavelengths.  For full credit, show your work.
:::
:::Question
Which element is in this lamp?  Explain your reasoning.
:::

* Repeat for the other lamp.
:::Question
In order of brightness, starting with the brightest, what are the $\theta_1$ values of those four lines?  What are their wavelengths.  For full credit, show your work.
:::
:::Question
Which element is in this lamp?  Explain your reasoning.
:::

:::

<hr>
#### (Click on the footnote number to return to its position in the main text.)

[^1]: Interestingly, the measured value of $R$ did not match the prediction of the simplest Bohr model which uses $m = m_e$ because the electron and proton together lead to an effective “reduced mass”, $m$, that is very slightly below the electron mass. Furthermore, the spectrum of hydrogen was found to contain a set of wavelengths with a slightly different $R$ value. These come from deuterium, which is hydrogen with a neutron in the nucleus, the mass of which further alters $m$). Both effects are smaller than 0.1% and only revealed by exquisitely precise measurements.

[^2]: It is amusing to note how often dialogue in Star Trek episodes involves the captain asking for a “multi-spectral analysis” of some anomaly. Analyzing the spectrum of astrophysical objects is common, in fact so common that it would be done automatically, without the captain’s specific request! But it does provide tech-y sounding, and in this case not incorrect, dialogue.

[^3]:  To validate your results, it is good practice to measure $\theta_m$ values for other values of $m$, but be aware that the grating is optimized for $m=+1$, so the other maxima can be hard to see.

[^4]: If the collimated light hits the diffraction grating at some other angle $\theta_i \neq 0$, the equation becomes
$d (\sin \theta_i \mp \sin \theta_{\pm m}) = \pm m\lambda$, where the angles are measured from the grating's normal.  If $\theta_i \gg 0^\circ$ and you neglect the $\theta_i$-term, you will have a systematic error in your wavelength measurements.  Fortunately, it is easy to either (*i*) determine $\theta_i$  directly using the overview camera, which is positioned directly above the grating's axis of rotation, or (*ii*) cancel out its effect by measuring $\theta$ for two different values of $m \neq 0$ for the same wavelength and substracting the corresponding equations to cancel out the $\theta_i$-term.

[^5]: This value takes into account the effective reduced mass of the electron in the Hydrogen atom. [See Wikipedia for elaboration.](https://en.wikipedia.org/wiki/Rydberg_constant)

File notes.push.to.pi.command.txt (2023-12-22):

Push to pi command

rsync -r <directory to push> pi@<ip address>:~/

Must be run from directory containing remoteLabs, or path must be specified

For example, for FH, from within the “web interfacing” directory on my MacBookPro

rsync -r remoteLabs pi@128.111.18.10:~/

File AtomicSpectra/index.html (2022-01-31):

# Atomic Spectra Experiment

This session will end and the system will reset in 3:00:00 hours.

Telescope:

Grating:

Fine

Medium

Coarse

Fine

Medium

Coarse

(click to toggle the
ambient Light)
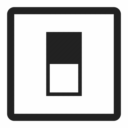
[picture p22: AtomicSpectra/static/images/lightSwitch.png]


### Schematic

(choose Fine/Coarse and click arrows to rotate the telescope or the grating)

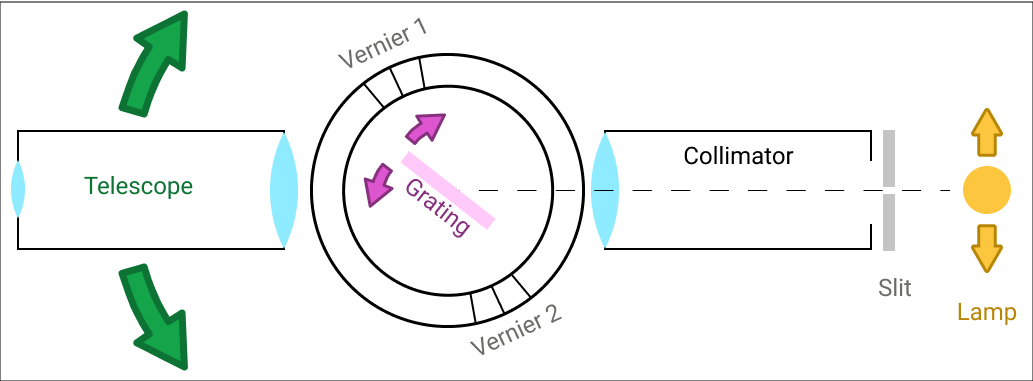
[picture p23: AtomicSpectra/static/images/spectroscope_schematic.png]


(click arrows to nudge the lamp)

(click to toggle the
Background dark)
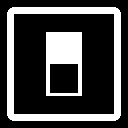
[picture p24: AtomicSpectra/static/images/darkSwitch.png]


Movable schematic

×

Telescope:

Grating:

Lamp:

Fine

Medium

Coarse

Fine

Medium

Coarse













Overview Eyepiece Vernier 1 Vernier 2

Transmission Grating  (https://www.patonhawksley.com/product-page/te215)

(click for grating info)



(click to toggle crosshairs visibility; move mouse over video to position crosshairs)

Instrument: AO Spencer Spectrometer

(click on image for a PDF of the Manual)

Spectrum Tube Lamps
   
(click on a lamp to rotate it into position or turn it on/off)



Fine

Coarse

(choose increment and click arrows to adjust slit width)

Camera Controls

× Exposure in Microseconds: 6000
Brightness: 50%
Contrast: 0%

Unknowns "A" and "B" are each one of the five Noble gases.

Select Picture type

Brightest Lines

All Lines



##### Page Loading

Please wait while the page finishes loading.

##### Motor Moving

The slit takes 5-20 seconds to adjust please be patient. This pop up will go away when it should be done moving.

##### Motor Moving

The lamp carousel takes 15-30 seconds to adjust please be patient. This pop up will go away when it should be done moving.

##### Limit Reached!

This object can't move any more in that direction.

##### STOP!



Before continuing the lab please send a message using the equipment help button at the bottom right of the screen



##### STOP!



You are about to be booted! You have 10 seconds to finish taking measurements. If this is a mistake use the equipment help button at the bottom right of the screen.




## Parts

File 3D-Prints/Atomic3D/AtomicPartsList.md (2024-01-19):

Atomic Spectroscopy has 12 Fusion 360 files

Atomic Spectroscopy was the first lab to heavily use 3D printed parts for a complicated assembly. Thus, its files are disjointed and not well organized. It has also had the most revisions over time. There are many files for individual components instead of a streamlined assembly like Diffrac or Gamma. 

*** Add a thorough description of the Atomic Lab ***

Camera Mount
	- Camera Mount
	- IR Camera 3 Legged Mount
	- IR Camera Mount
	- Telescope Mount
	- Vernier Cam 3 Legged Mount

Encoded Motor Drive Gear
	- Telescope Gear Idler
	- Telescope Gear

Infrared Sensor Mount (Sam)
	- Flag (Sam)

Optical Sensor (Sam)
	- Sensor Mount

Limit Switch Mounts
	- Limit Switch Mount

Slit Clip
	- Slit Clip

Spacer 
	- Spacer

Lamp Carousel Breadboard Mount
	- Carousel Stand Left
	- Carousel Stand Right

Dovetail Diffraction Grating Motor Mount
	- Grate Motor Mount (Motor)
	- Grate Motor Mount (Telescope)

Spectroscope Motor Mount .25-20 Edit
	- Telescope Motor Mount

Spectroscope Motor Mount
	- Slit Mount (Motor)
	- Slit Mount (Telescope)

Vernier Double Camera Mount
	- Vernier Double Cam Mount

1_4 Rod Foot
	- 1_4 Rod Foot

Deborah Notes: 

CarouselTop - anchors an encoded motor atop the carousel with its axis positioned vertically and the microcontroller off to the side.

CarouselArm - connects the motor shaft to the lamp turret

(list all the rest of the 3D printed items used in this setup)

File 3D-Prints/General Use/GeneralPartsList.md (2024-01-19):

The General Parts directory has files for mounts, cameras, assemblies, and other general purpose files used in multiple labs. 

T-slot hardware can be found in the Gamma lab files
Alternate camera mounting hardware can be found in the Atomic Spectroscopy lab files

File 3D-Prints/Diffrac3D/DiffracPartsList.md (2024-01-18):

Diffraction Interference has 3 primary Fusion 360 files:
	Mounting System Version 3
	Track Center and Guide
	Direct Drive Slit Mount

The fourth file, Track Screen Mount, is generally used in the in-person lab to mount screens, phones, cameras, to the DI track. This file is also available to serve as a general template for mounting things to the DI Track.

The DI lab consists of 2 main parts mounted on one optics rail. The first part is the laser and slit assemblies. This section allows us to control the laser and the particular slit through which the laser passes. All files for this are in the 'Direct Drive Slit Mount' Fusion 360 file. This Direct Drive system interfaces with stepper motors and requires mounting hardware. The second part is the moving stage with the screen/camera mounting system. The guides that help center and level the stage are found in the 'Track Center and Guide' Fusion 360 file. The 'Mounting System Version 3' fusion file contains everything that mounts to the moving stage. This contains the screen mounting frame, the rear camera mount, and a mount for a downwards facing camera used to measure the distance between the screen and the slits. This system requires 1/4 inch rods and mounting screws. 

Mounting System Version 3
	This file includes the entire assembly on top of the moving stage. 
	- Screen Frame Front
	- Screen Frame Back
	- Tape Camera Bottom
	- Tape Camera Top
	- Horizontal Dovetail Camera Mount
	- Horizontal Dovetail Rod Mount

Track Center and Guide
	Contains only two relevant pieces, one to center the stage on the optics rail, and the second to center and support the stage off the end of the optics rail at the correct height. 
	- Stage Guide
	- Stage Table Mount
	
Direct Drive Slit Mount
	Contains mounting pieces needed to direct drive mount the stepper motors to the diffraction wheels on the optics rail mounts. Also includes identifying rings for each slit wheel useful for calibration and visualizing position. The final relevant pieces are the guides for the wheels, these turned out to be unnecessary 
	- Direct Drive Motor Junction
	- Direct Drive Motor Mount
	- Labeled DS Ring
	- Labeled SS Ring

Deborah Notes: 

StageMount - anchors the screen to the translation stage.

ScreenFrame - holds switchable plastic screen.

(list all the rest of the 3D printed items used in this setup)

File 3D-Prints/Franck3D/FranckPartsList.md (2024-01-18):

Franck Hertz has 5 Fusion 360 files:
	DCV Clip
	FH Pulley
	L Bracket
	Variac Idler
	Variac Pulley

The Franck Hertz lab does not have a well defined print repository like other labs. It was the first lab to be remotified and was mostly done manually. It should get a complete 3D printed redesign, particularly for the motors. Thus, all the files are somewhat disjointed.

DCV Clip
	Clip to mount the DCV and DCA
	- DCV Clip

FH Pulley
	- Pulley

L Bracket
	- L Brakcet

Variac Idler
	- Variac Idler Arm
	- Idler Bearing

Variac Pulley
	- Variac Pulley

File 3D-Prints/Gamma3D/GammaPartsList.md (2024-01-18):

Gamma Radiation has 5 primary Fusion 360 files:
	GR T-Slot Frame Brackets
	Stage Mount
	Shielding Holder
	Absorber Mounts
	Servo Actuator Mount

The GR lab consists of 3 main parts: the T-Slot frame, shielding/source holder assembly, and the servo actuator assembly. The GR T-Slot frame files are all usable in any T-Slot assembly, however, they were designed for the gamma lab. The stage mount is specifically designed to mount the linear moving stage to T-Slot cross bars. The shielding holder simply holds all of the absorbers and sources  as well as includes a tapered frame to increase success when loading into the counter. The Absorber Mounts file includes past versions of the frames as separate components. The frame gap can be adjusted using the parameter "FrameIndent". Servo Actuator Mount is the complex assembly that grabs the absorbers and loads them into the counter. 

GR T-Slot Frame Brackets
	T-Slot frame hardware
	- Concealed Bracket
	- Perpendicular Bracket
	- L Bracket
	- Flat Guard Long

Stage Mount
	Linear stage to T-Slot mount
	- Stage Mount

Shielding Holder
	Housing for absorbers and sources, and faceplate for geiger counter
	- Shielding Holder
	- Geiger Counter Faceplate

Absorber Mounts
	Custom 3D printed frames to have the same end dimensions. Adjust "FrameIndent" parameter to fit absorbers of different thicknesses.
	- Frame 0.6mm
	- Frame 1.0mm
	- Frame 1.4mm
	- Source Holder
	- Magnet Clip

Servo Actuator Mount
	Assembly for grabbing absorbers and loading them into the counter and holder
	- Cart Base
	- Large Gear
	- Small Gear
	- T-slot Rail Long
	- Grabber
	- Push Pin
	- Frame Guide

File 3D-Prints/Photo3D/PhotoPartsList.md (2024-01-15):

Photoelectric Effect only has 2 Fusion 360 files:
	Double Nema 17 Motor Mount
	PE Filter Riser

The PE Filter Riser is used just to rest the filter wheel high enough for the belts to fit under the filter wheels.
	- Filter Riser

The Double Nema 17 Motor Mount is designed to allow stacking of Nema 17s so that we can belt drive the filter wheel and the ND wheel with a smaller footprint. This requires specific screw hardware as the posts are designed for 2 inch screws (I believe).
	- Dual Motor Mount Bottom Base
	- Dual Motor Mount Top Base

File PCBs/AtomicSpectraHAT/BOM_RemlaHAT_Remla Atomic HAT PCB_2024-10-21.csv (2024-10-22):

No. | Quantity | Comment | Designator | Footprint | Value | Manufacturer Part | Manufacturer | Supplier Part | Supplier
1 | 1 | XH-2AW | 5V_OUT | CONN-TH_2P-P2.50_XH-2AW |  | XH-2AW | BOOMELE(博穆精密) | C33132 | LCSC
2 | 3 | NCD0805G1 | 5V_PG,ARM_ON,CR_ON | LED0805-R-RD |  | NCD0805G1 | 国星光电 | C84260 | LCSC
3 | 2 | B2B-XH-A(LF)(SN) | 12V_OUT,12V_PWR | CONN-TH_B2B-XH-A-LF-SN |  | B2B-XH-A(LF)(SN) | JST | C158012 | LCSC
4 | 1 | 2.54-1*2P母 | AMBIENT_LED | HDR-TH_2P-P2.54-V-F |  | 2.54-1*2P母 | BOOMELE(博穆精密) | C49661 | LCSC
5 | 1 | PZ254-2-13-Z-8.5 | ARDUCAM_CARD | HDR-TH_26P-P2.54-V-M-R2-C13-S2.54 |  | PZ254-2-13-Z-8.5 | HCTL(华灿天禄) | C2894974 | LCSC
6 | 2 | NCD0805R1 | ARM_OFF,CR_OFF | LED0805-R-RD |  | NCD0805R1 | 国星光电 | C84256 | LCSC
7 | 2 | 100uF | C1,C2 | CAP-TH_BD5.0-P2.00-D0.8-FD | 100uF | KS107M016D07RR0VH2FP0 | CX(承兴) | C43803 | LCSC
8 | 3 | 10uF | C3,C4,C5 | C0805 | 10uF | CL21A106KOQNNNE | SAMSUNG(三星) | C1713 | LCSC
9 | 3 | 22uF | C6,C7,C8 | C0805 | 22uF | CL21A226MAQNNNE | SAMSUNG(三星) | C45783 | LCSC
10 | 3 | 10uF | C9,C12,C13 | C0603 | 10uF | CL10A106KP8NNNC | SAMSUNG(三星) | C19702 | LCSC
11 | 1 | 100nF | C10 | C0402 | 100nF | CC0402KRX7R7BB104 | YAGEO(国巨) | C60474 | LCSC
12 | 1 | 100nF | C11 | C0603 | 100nF | CC0603KRX7R9BB104 | YAGEO(国巨) | C14663 | LCSC
13 | 1 | 1.5uH | L1 | IND-SMD_L4.0-W4.0-A | 1.5uH | XFL4020-152MEC | Coilcraft(线艺) | C3033018 | LCSC
14 | 1 | AO3400A_N | Q3 | SOT-23-3_L2.9-W1.3-P1.90-LS2.4-BR |  |  |  | C700953
15 | 2 | 10kΩ | R1,R5 | R0603 | 10kΩ | 0603WAF1002T5E | UNI-ROYAL(厚声) | C25804 | LCSC
16 | 3 | 1kΩ | R2,R3,R6 | R0603 | 1kΩ | 0603WAF1001T5E | UNI-ROYAL(厚声) | C21190 | LCSC
17 | 2 | HC-XH-6A-G | S42C_ARM,S42C_CR | CONN-TH_6P-P2.50_HC-XH-6A-G |  | HC-XH-6A-G | HCTL(华灿天禄) | C5341205 | LCSC
18 | 2 | SS12D10G5 | U1,U2 | SW-TH_SHOU-HAN_SS12D10G4 |  | SS12D10G5 | SHOU HAN(首韩) | C7431054 | LCSC
19 | 1 | TPS630701RNMR | U3 | VQFN-HR-15_L3.0-W2.5-P0.50-BL_TPS63070RNMR |  | TPS630701RNMR | TI(德州仪器) | C2876599 | LCSC

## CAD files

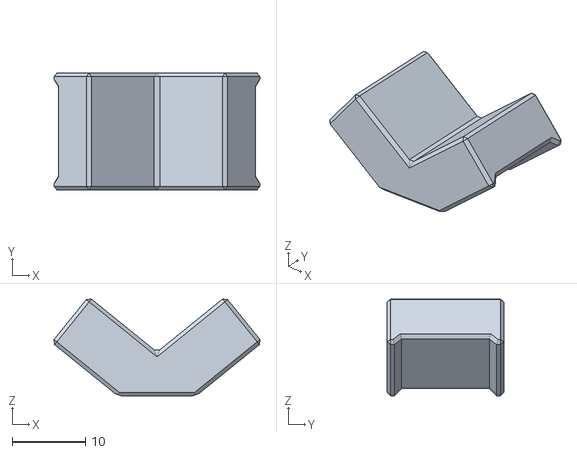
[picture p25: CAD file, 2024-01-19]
3D-Prints/20L Files/Phone Mount Eyepiece Spacer (AS)/Lipped Spacer.stl
28.2 x 16.0 x 13.3

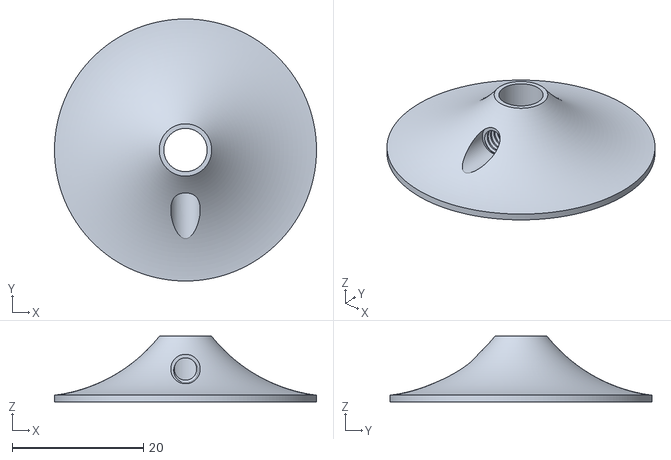
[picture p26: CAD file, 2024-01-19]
3D-Prints/Atomic3D/1_4 Rod Foot/1_4_ Rod Foot v2.stl
40.0 x 40.0 x 10.0

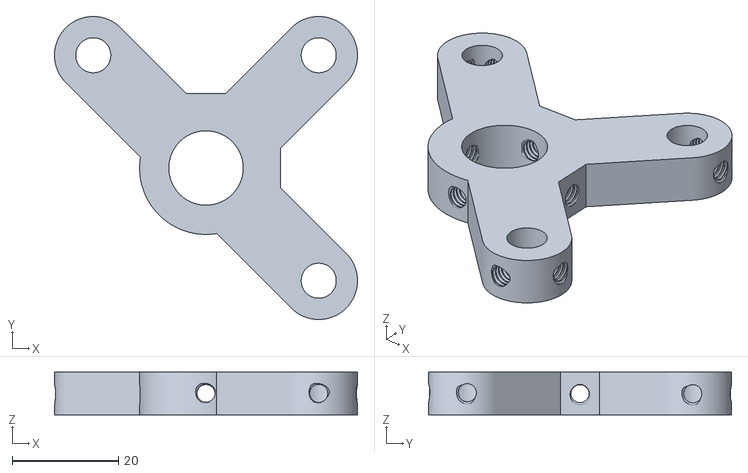
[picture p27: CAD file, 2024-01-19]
3D-Prints/Atomic3D/Camera Mount/STL Files/AS Vernier Cam 3 Legged Mount.stl
57.0 x 57.0 x 8.00

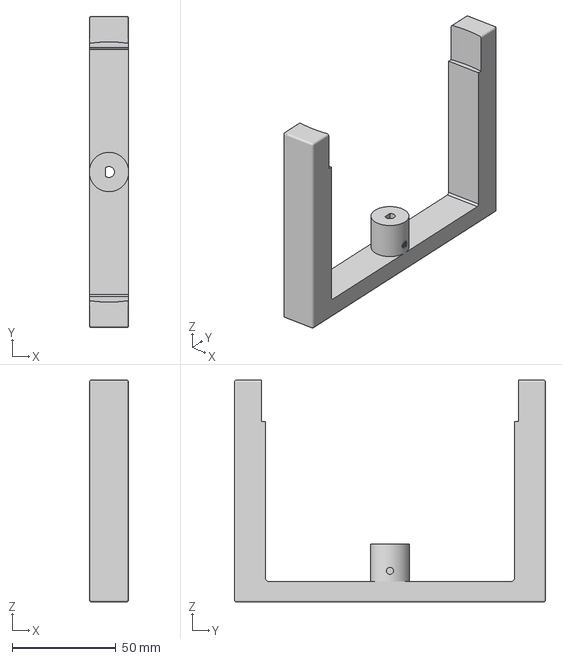
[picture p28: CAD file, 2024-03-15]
3D-Prints/Atomic3D/Carousel Arms/Carousel Arm Encoded Motor.3mf
19.0 x 150.0 x 107.0 mm

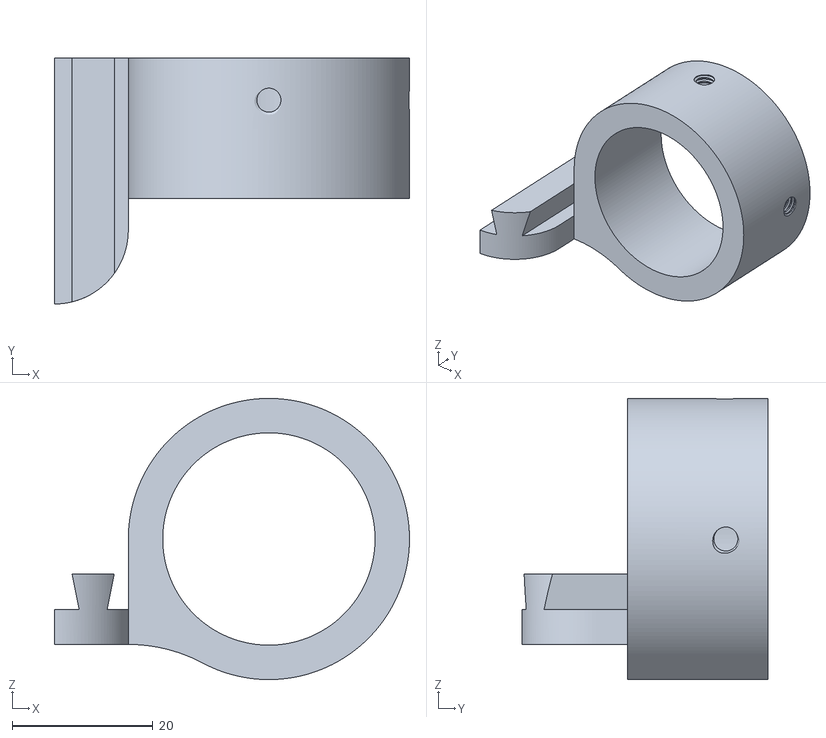
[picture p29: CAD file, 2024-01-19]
3D-Prints/Atomic3D/Dovetail Diffraction Grate Motor Mount/AS Grate Motor Mount (Telescope).stl
50.5 x 35.0 x 40.0

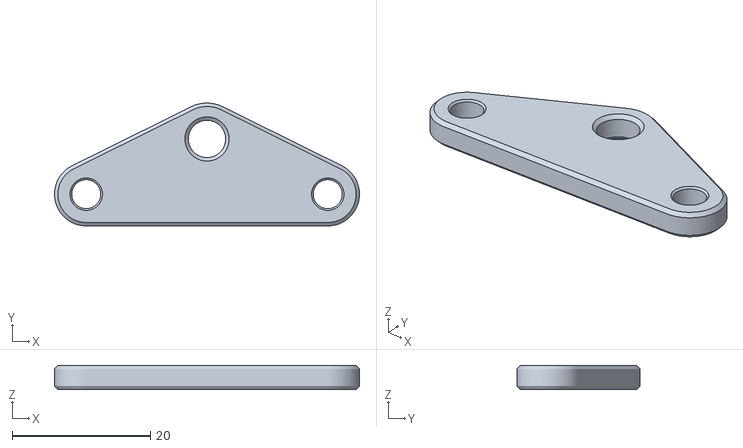
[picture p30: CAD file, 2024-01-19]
3D-Prints/Atomic3D/Encoded Motor Drive Gear/AS Telescope Gear Idler.stl
44.2 x 17.8 x 3.50

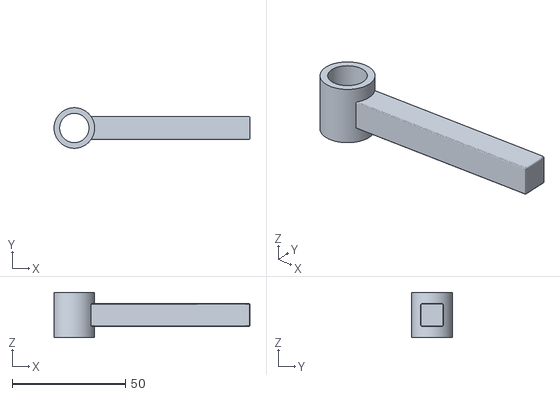
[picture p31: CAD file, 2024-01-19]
3D-Prints/Atomic3D/Infrared Sensor Mount (Sam)/AS Flag (Sam).stl
86.4 x 17.9 x 20.0

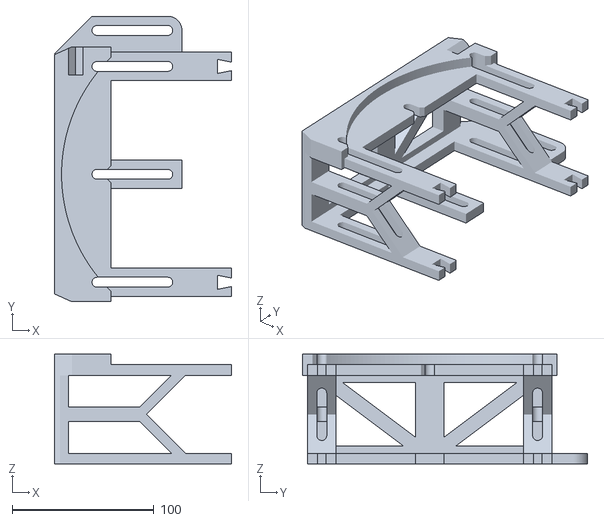
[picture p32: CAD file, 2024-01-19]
3D-Prints/Atomic3D/Lamp Carousel Breadboard Mount/AS Carousel Stand Left.stl
125.0 x 201.6 x 77.5

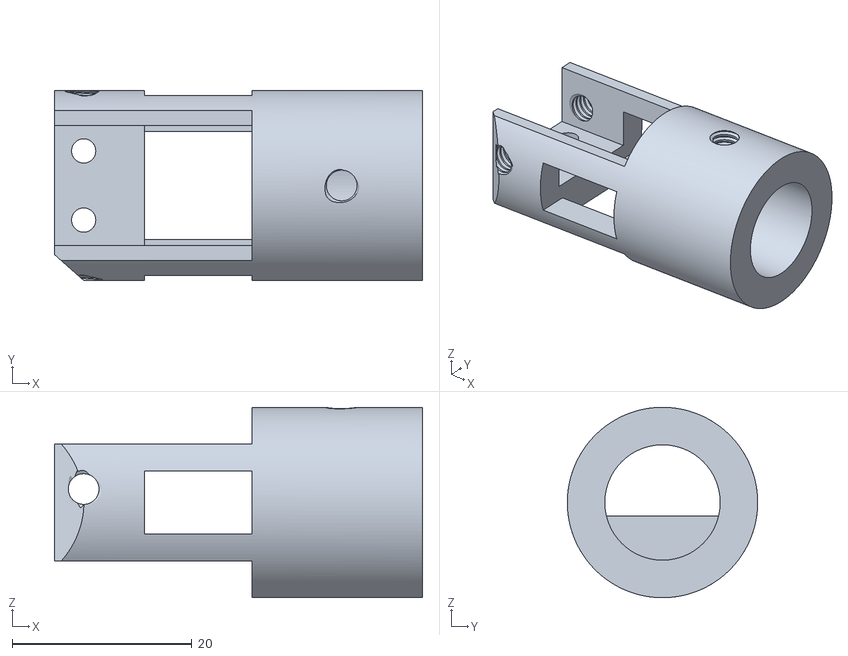
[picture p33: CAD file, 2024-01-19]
3D-Prints/Atomic3D/Limit Switch Mounts/AS Limit Switch Mount.stl
41.0 x 21.2 x 21.2

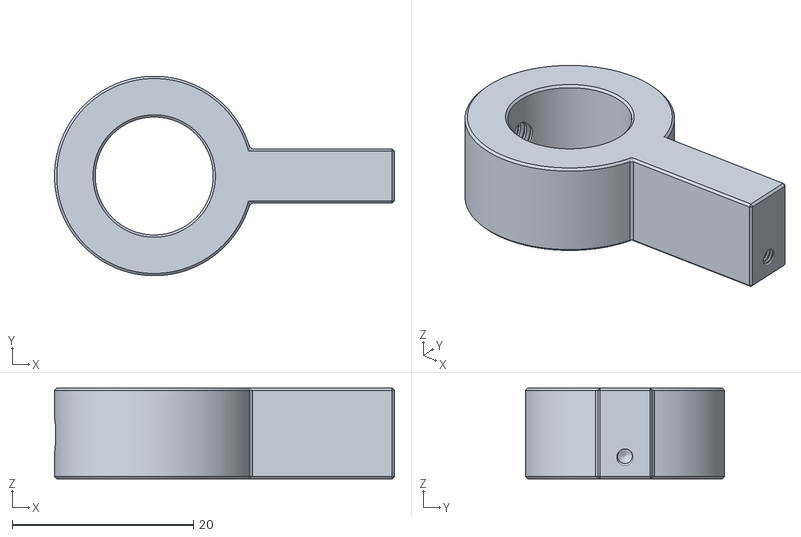
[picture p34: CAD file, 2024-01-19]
3D-Prints/Atomic3D/Optical Sensor (Sam)/AS Sensor Mount (Sam).stl
37.5 x 22.0 x 10.0

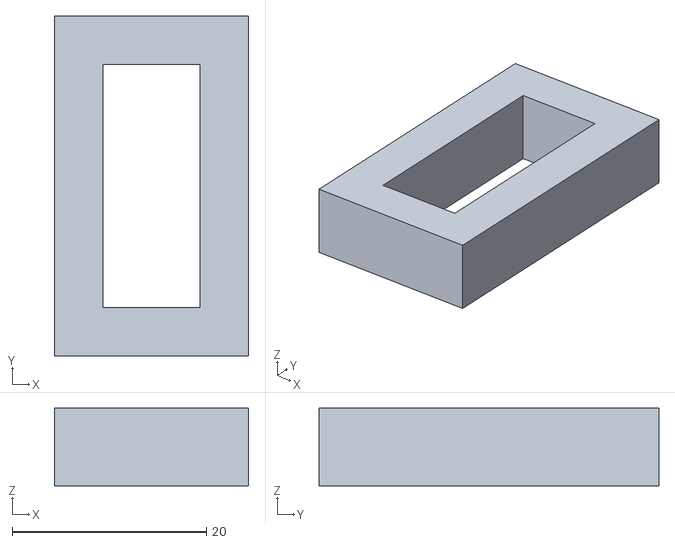
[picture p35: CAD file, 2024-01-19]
3D-Prints/Atomic3D/Spacer/AS Spacer.stl
20.0 x 35.0 x 8.00

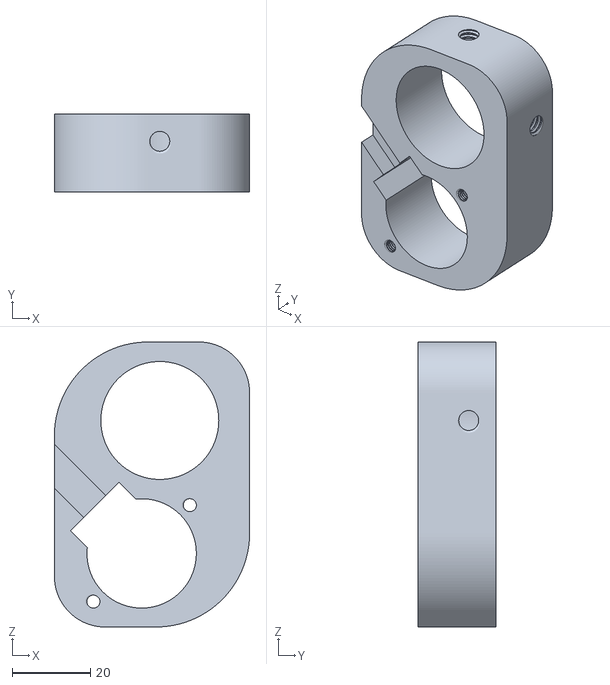
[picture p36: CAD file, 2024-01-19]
3D-Prints/Atomic3D/Spectroscope Motor Mount .25-20 Edit/AS Telescope Motor Mount.stl
50.0 x 20.0 x 73.0

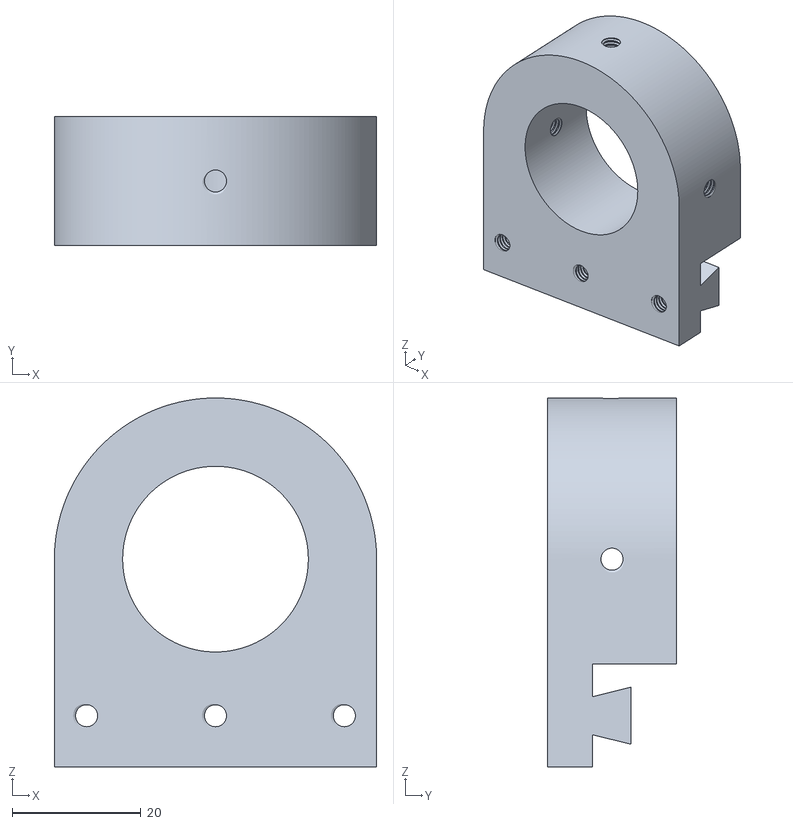
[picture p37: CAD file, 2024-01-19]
3D-Prints/Atomic3D/Spectroscope Motor Mount/AS Slit Mount (Telescope).stl
50.0 x 20.0 x 57.2

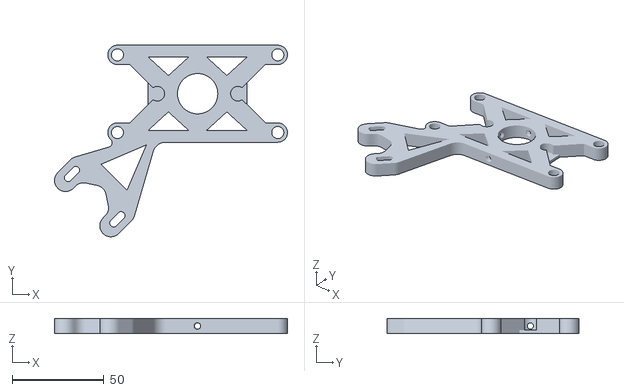
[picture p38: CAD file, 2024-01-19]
3D-Prints/Atomic3D/Vernier Double Camera Mount/AS Vernier Double Cam Mount.stl
127.3 x 104.7 x 8.00

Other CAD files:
3D-Prints/Broida Welcome Event/Decoder/Decoder Top.stl
3D-Prints/Diffrac3D/Direct Drive Slit Mount/STL/DI Labeled DS Ring.stl
3D-Prints/Diffrac3D/Mounting System Version 3/STL Files/DI Screen Frame Front.stl
3D-Prints/Diffrac3D/Track Center and Guide/STL/DI Stage Guide.stl
3D-Prints/20L Files/20BL Top/20BL Top v5.f3d
3D-Prints/20L Files/Phone Mount Eyepiece Spacer (AS)/Phone Mount Eyepiece Spacer v2.f3d
3D-Prints/20L Files/Phone Mount Eyepiece Spacer (AS)/Spacer.stl
3D-Prints/Atomic3D/1_4 Rod Foot/1_4 Rod Foot v3.f3d
3D-Prints/Atomic3D/Camera Mount/Camera Mount v8.f3d
3D-Prints/Atomic3D/Camera Mount/STL Files/AS Camera Mount.stl
3D-Prints/Atomic3D/Camera Mount/STL Files/AS IR Camera 3 Legged Mount.stl
3D-Prints/Atomic3D/Camera Mount/STL Files/AS IR Camera Mount.stl
3D-Prints/Atomic3D/Camera Mount/STL Files/AS Telescope Mount.stl
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

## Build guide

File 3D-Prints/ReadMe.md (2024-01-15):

This directory contains the custom parts designed and printed for the UCSB Physics Remote Labs. Parts for each remote lab were designed in Fusion 360 and 3D printed using Fused Deposition Modeling (FDM) on Prusa printers. Some labs have a primary Fusion 360 file with multiple assemblies and some files have only individual pieces.

Each lab (and general) has a sub directory with all relevant Fusion 360 files, STL files, 3MF PrusaSlicer Projects, an Gcode files. The .gCode will be for Prusa Mini+ printers with 0.4mm nozzle and include photo of the final part both alone and in its context in the setup.

Organization is as follows:
3D - Printing
  Lab
    Fusion 360 File
	STL, 3MF, GCode files derived from above Fusion file

File Structure Outline
	1. Lab Files
		a. All files associated with a specific lab will go here
		b. One sub folder for each Fusion 360 file
			i. Name Format: 'File Name' (include date edited?)
			ii. Includes a Readme which describes the relevant files
			iii. Includes Fusion 360 file
			iv. Subfolders:
				I. STL Files
				II. PrusaSlicer Projects
				III. GCode Files
		c. One additional sub folder to house all old Fusion 360 files
			i. Name Format: Old Files
			ii. Contains old Fusion 360 files
		d. Photos for each part sub directory with matching name
			i. Each photo includes the Fusion 360 outline to show all 'Components'
		e. Include videos and photos of the lab set up as a whole
	2. General Files 
		a. All files not associated with a specific lab (files used across labs)
		b. One sub folder for each Fusion 360 file
			i. Name Format: 'File Name'_YYMMDD
			ii. Includes a Readme which describes the relevant files
			iii. Includes Fusion 360 file
			iv. Subfolders:
				I. STL Files
				II. PrusaSlicer Projects
				III. GCode Files
		c. One additional sub folder to house all old Fusion 360 files
			i. Name Format: Old Files
			ii. Contains old Fusion 360 files
		d. Include videos and photos of the lab set up and the printed parts.

Sample File Structure
	1. Unprojected Footage
		a. 20703_ShorelinePark_Mini3Pro_Random_Sunset
			i. Videos
			ii. Photos
			iii. Hyperlapse
		b. 220920_Sands_Mini3Pro_PlatformHolly_Night
			i. Videos
		c. 210321_GarrapataVistaPoint_Mini_Random_Day
			i. Videos
			ii. Hyperlapse
	2. Projected Footage 
		a. Garrapata Vista Point 220814
			i. Videos
				- 210321_GarrapataVistaPoint_Mini_Random_Day
			ii. Sounds
			iii. Other Assets
			iv. Final Output
			v. Garrapata (FCPX File)

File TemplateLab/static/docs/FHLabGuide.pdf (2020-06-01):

# Physics 25L lab manual

### Professor Deborah K Fygenson, UCSB Physics Department

This is a modified version of the original manual written by Professor David Stuart

### May 9, 2020

## Contents

1 Introduction to Experimental Methods | 3
1.1 Uncertainties | | 3
1.1.1 Estimating uncertainties | | 4
1.1.2 Propagating uncertainties | | 6
1.1.3 Plotting and fitting | | 7
1.2 Validation of results | 10
1.3 Rigorous record keeping | 12
1.4 Excelling | 14
2 Gamma ray absorption | 16
2.1 Pre-lab preparation | 16
2.1.1 Interaction of radiation with matter | 17
2.1.2 Apparatus | 18
2.1.3 Safety and care of equipment | 20
2.2 Getting started and gaining familiarity | 20
2.3 Measuring the mass absorption length | 21
2.4 Data analysis | 22
2.4.1 Beware biases | 24
2.4.2 A concise summary of results | 25
2.5 Going Beyond | 26
3 Interference and Diffraction | 27
3.1 Pre-lab preparation | 27
3.1.1 Experimental planning | 30
3.1.2 Apparatus | 31
3.1.3 Safety | 32
3.2 Getting started and gaining familiarity | 32
3.3 Qualitative observations of interference and diffraction | 32
3.4 Measurement of the wavelength of a laser | 32
3.4.1 Image analysis | 34
3.4.2 Putting it all in your logbook | 34
3.5 Going beyond | 34
4 The Photoelectric Effect, Photons and Planck’s constant | 36
4.1 Pre-lab preparation | 36
4.1.1 Apparatus | 37
4.1.2 Safety | 38
4.2 Getting started and gaining familiarity | 39
4.2.1 Operation of the electrometer | 40
4.3 Measure Vs(⌫) and extract h | 41
4.4 Going Beyond | 41
5 Atomic spectra and the Rydberg constant | 43
5.1 Pre-lab preparation | 43
5.1.1 Apparatus | 44

5.1.2 Safety and care of equipment | 46
5.2 Getting started and gaining familiarity | 46
5.3 Measuring the spectrum and extracting Rydberg’s constant | 47
5.4 Measuring the spectrum of an unknown source | 47
5.5 Going Beyond | 48
6 The Franck-Hertz experiment | 78
6.1 Pre-lab preparation | 78
6.1.1 Apparatus | 79
6.1.2 Safety and care of equipment | 80
6.2 Getting started and gaining familiarity | 80
6.3 Measuring the excitation energy | 81
6.4 Going Beyond | 82

## 6 The Franck-Hertz experiment

Abstract: In this lab you will measure the first excitation energy of Mercury by carrying out a modern version of the landmark experiment reported by James Franck and Gustav Hertz in 1914.

### 6.1 Pre-lab preparation

In the atomic spectra lab, you saw that atoms emit photons of specific, quantized energies. In this lab, you will see that they also absorb energy in quantized amounts from electrons.
Franck and Hertz didn’t set out to validate quantum theory. They conceived the experiment in 1911, well before Niels Bohr proposed his model of the atom, with the aim of better understanding electron conductivity through gases. But by the time they built their experiment, collected their data and reported their results it was 1914. The Bohr model was about one year old. Their data offered unequivocal evidence that an atom can accept energy only in discrete amounts. It was crucial to the acceptance of quantum theory because, at that time, photons were still somewhat mysterious but electrons were unquestionably real particles whose kinetic energy could be readily determined.
The experiment generates a current of electrons from a cathode and accelerates them with a voltage on an anode, Va, so the maximum kinetic energy that can be obtained by the electrons is eVa. A low pressure gas of mercury atoms in the region between the cathode and anode causes the moving electrons to scatter off the mercury atoms. If the atoms could absorb any energy from the electrons, we’d expect that the electrons would lose energy even when they are moving slowly. But, if the atoms can only absorb discrete energies from the electrons, then we’d expect to see a sudden onset of energy transfer only once the electrons’ kinetic energy becomes equal to the lowest (or first) excitation energy of the mercury atoms. By slowly increasing Va and measuring the kinetic energy of the electrons that reach the anode, we can test this expectation. A sudden drop should occur when eVa reaches the first excitation energy eV1.
If the voltage is increased above V1, an electron that excites a mercury atom in one collision can regain energy after the collision. When Va reaches 2V1, it becomes possible for an electron to undergo two interactions, and be left with little energy when it reaches the anode. This continues as the voltage is increased further; we should see drops in the electrons’ final kinetic energy each time Va crosses an integer multiple of mercury’s first excitation energy.
There are two complications in the actual experiment. First, it is not easy, or necessary, to directly measure the final kinetic energy of the electrons. It is simpler, and sufficient, to just measure how many electrons are above some kinetic energy threshold. We can do that by using a grid for the anode, so the electrons can pass through it, and then placing a third electrode beyond it. Applying a retarding voltage, Vr >Va, to that third electrode will allow only electrons with kinetic energy above e(Vr Va) to reach it. (Ask yourself: Where will the other electrons go?) Measuring the current collected by the third electrode will measure how many electrons have sufficient kinetic energy to reach it. We can detect when there is a drop in electron kinetic energy due to excitation of the mercury atoms by observing a drop in the current through the “collection electrode”.
The second complication is that there are small offsets to the kinetic energy of the electrons due to the contact potential of the electrodes. For example, the thermionic emission of electrons from the cathode requires a small amount of energy, similar to the work function of the metal that we encountered in measurements of the photoelectric effect. The voltage when the first drop occurs is not a good measure of V1 due to bias from these offsets. However, measuring the difference in voltage between subsequent current drops removes the bias and can be used to determine V1.

### 6.1.1 Apparatus

A diagram of the apparatus you’ll use is shown in Figure 21. A photo of the apparatus you’ll use is shown in Figure 22. In the diagram, the volume containing gas is depicted as an ellipse. The cathode, with its heater, is at the bottom of the volume, both in the diagram and inside the apparatus. The anode grid is represented by a thick, dashed line, and above it the collection electrode is represented by a thick, solid line. The gas volume is housed within an oven that is heated by the power supply at the upper left, and its power is controlled by the large variac. To produce thermionic emission, the cathode is heated by a filament controlled by the smaller variac, shown at the bottom left. The anode voltage, Va, is set by the power supply, and adjusted with a variable resistor. The retarding voltage on the collection electrode, Vr, is set by a 1.5 V battery with a variable resistor. Each of the voltages, Va and Vr, are measured by voltmeters. The current reaching the collection electrode is measured by the electrometer, which is the same device you used in the photoelectric effect lab.

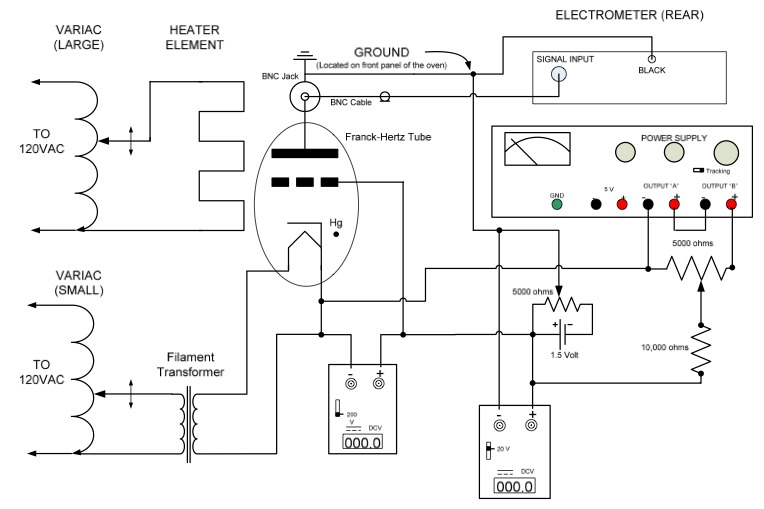
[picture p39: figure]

Figure 21: Diagram of the apparatus.

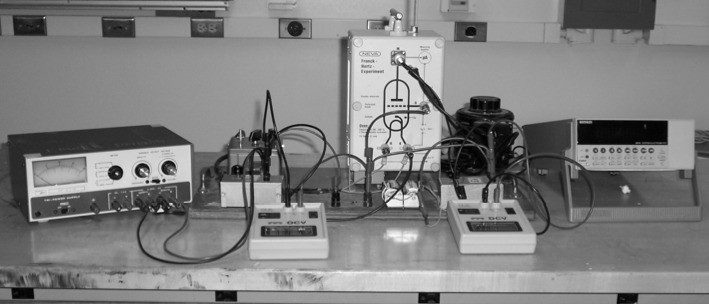
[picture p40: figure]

Figure 22: Photo of the apparatus.

### 6.1.2 Safety and care of equipment

The potential hazards in this lab involve the high temperature of the oven and the moderately high voltage of the power supply. Both hazards are mitigated by being contained within enclosures.

### 6.2 Getting started and gaining familiarity

The first thing to do is insert the thermometer into the oven so that its bulb is even with the mid section of the tube. Then turn the oven on. (Both of these things may have been done for you, as it takes the oven, and the room itself, a while to stabilize in temperature.) The target temperature is in the 170 190C range. It can be adjusted with the large variac knob. You should set it initially to about “78” on the variac’s scale, but monitor the temperature frequently and adjust accordingly. Note that the thermal response time is large. It may take 10 - 15 minutes to warm up, and adjusting the variac knob will not cause an immediate change. It is best to make small changes and monitor frequently.
Check the setup and confirm that it is wired as shown in Figure 21(a). Ask for assistance if anything does not make sense.
Turn on the electrometer and correct any zero offsets. The procedure for this is the same as in the photoelectric effect lab, and is listed again, for your convenience, in Figure 23.
Once the oven temperature has stabilized at about 180C, set the retarding potential to 1.3 V and then turn on the power supply. Be sure that the power supply is set to “Tracking mode” and the output voltage is set to 40 V (far right knob, or “master control”, depending on the power supply model). Then adjust the 5k⌦ potentiometer that controls Va up until you measure about 40 V on Va’s voltmeter.
Set the knob on the small variac to zero and then turn on the small variac. This variac controls the cathode’s filament heater, which causes electrons to be thermionically emitted from the cathode. Slowly increase the small variac’s knob until you get a current reading on the electrometer of between 0.75 and 1.0 nA, but don’t go beyond that current. Caution: if you exceed 1 nA before the variac has been turned more than about halfway, shut it off immediately and notify the TA.

Zero Correction procedure to remove offsets
- Enable Zero Check mode. Press ZCHK; you should see a “ZC” message appear at the right side of the display.
- Select the current measuring mode by pressing I (if not already in that mode).
- Select the appropriate measurement range.
- Perform a zero correction by pressing ZCOR; you should see a “ZZ” message appear in the display.
- Press ZCHK to disable the Zero Check mode; you should now see a “CZ” message appear in the display to indicate that the subsequent readings are corrected for any zero point offsets.
Figure 23: Zero correction procedure.

Now that everything is on and functioning, you can begin making measurements.

### 6.3 Measuring the excitation energy

If you follwed the directions described above, Va is set to the highest value ( 40 V) you’ll want to use. Take a first round of data by reducing Va by 0.5 V at a time and noting the electrometer current, I. This is coarse measurement, so don’t bother waiting very long for the current to settle to a stable value. Give it a few seconds and just jot it’s value down. After you’ve collected a few dozen data points, in this crude way, plot your data. Write down salient details of what you notice in your logbook. Then go back to taking crude data until you get to Va =0 V. Again, plot your data and note any thoughts you have about it in your logbook. In particular, think about what clues this crude data offers for how you should go about taking precision data.
Make your first pass at taking precision data by increasing Va while monitoring I. It should increase at first, and then decrease after it crosses the point where electrons can excite mercury atoms. Collect data that will let you identify the Va at which I peaks. Make sure to describe your procedure for doing so in your logbook. Then continue to increase Va and you should see that the current goes through a minimum. Collect data that will let you identify the Va at which I is its lowest. Again, make sure to describe your procedure for doing so in your logbook.
Continue to increase Va and similarly record the voltage and current for each of the subsequent peaks and minima until you reach the maximum possible value of Va = 40 V. You should see about six cycles of current peaks and minima.
In addition to recording near the peaks and minima, you should record I and Va at a few points between them. This will allow you to make a plot of the full I(V ) curve that illustrates the overall behavior.
Determine the first excitation energy of mercury. Keep in mind that the absolute voltage is biased by potential offsets so, as explained in the introduction, instead of using the voltage values directly, you should use the differences between consecutive peaks or consecutive minima for your measurement.

### 6.4 Going Beyond

While you can obtain a measurement from a single scan, or even from just a couple peak positions, it is always a good idea to measure things repeatedly. Measuring the variation between multiple measurements helps to validate the results. You would be wise to take more than one scan.

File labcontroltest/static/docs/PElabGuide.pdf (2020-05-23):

# Physics 25L lab manual

### Professor Deborah K Fygenson, UCSB Physics Department

This is a modified version of the original manual written by Professor David Stuart

### May 9, 2020

## Contents

1 Introduction to Experimental Methods | 3
1.1 Uncertainties | | 3
1.1.1 Estimating uncertainties | | 4
1.1.2 Propagating uncertainties | | 6
1.1.3 Plotting and fitting | | 7
1.2 Validation of results | 10
1.3 Rigorous record keeping | 12
1.4 Excelling | 14
2 Gamma ray absorption | 16
2.1 Pre-lab preparation | 16
2.1.1 Interaction of radiation with matter | 17
2.1.2 Apparatus | 18
2.1.3 Safety and care of equipment | 20
2.2 Getting started and gaining familiarity | 20
2.3 Measuring the mass absorption length | 21
2.4 Data analysis | 22
2.4.1 Beware biases | 24
2.4.2 A concise summary of results | 25
2.5 Going Beyond | 26
3 Interference and Diffraction | 27
3.1 Pre-lab preparation | 27
3.1.1 Experimental planning | 30
3.1.2 Apparatus | 31
3.1.3 Safety | 32
3.2 Getting started and gaining familiarity | 32
3.3 Qualitative observations of interference and diffraction | 32
3.4 Measurement of the wavelength of a laser | 32
3.4.1 Image analysis | 34
3.4.2 Putting it all in your logbook | 34
3.5 Going beyond | 34
4 The Photoelectric Effect, Photons and Planck’s constant | 36
4.1 Pre-lab preparation | 36
4.1.1 Apparatus | 37
4.1.2 Safety | 38
4.2 Getting started and gaining familiarity | 39
4.2.1 Operation of the electrometer | 40
4.3 Measure Vs(⌫) and extract h | 41
4.4 Going Beyond | 41
5 Atomic spectra and the Rydberg constant | 43
5.1 Pre-lab preparation | 43
5.1.1 Apparatus | 44

5.1.2 Safety and care of equipment | 46
5.2 Getting started and gaining familiarity | 46
5.3 Measuring the spectrum and extracting Rydberg’s constant | 47
5.4 Measuring the spectrum of an unknown source | 47
5.5 Going Beyond | 48
6 The Franck-Hertz experiment | 78
6.1 Pre-lab preparation | 78
6.1.1 Apparatus | 79
6.1.2 Safety and care of equipment | 80
6.2 Getting started and gaining familiarity | 80
6.3 Measuring the excitation energy | 81
6.4 Going Beyond | 82

## 4 The Photoelectric Effect, Photons and Planck’s constant

Abstract: Two critical experimental observations led to the development of Quantum Mechanics: the blackbody spectrum and the photoelectric effect. In this lab you will explore the photoelectric effect and use it to measure Planck’s constant.

### 4.1 Pre-lab preparation

Quantum Mechanics was developed in the early 1900’s, but the evidence for it began to appear even in the late 1800’s. For example, Heinrich Hertz noticed that sparks started more rapidly when electrodes were illuminated with ultraviolet (UV) light. Other investigators later determined that free charges (i.e., electrons) were emitted from metal electrodes illuminated by UV light. These were called “photoelectrons”. Some metals, mostly the alkali metals in the first column of the periodic table, produced a steady supply of photoelectrons (called a “photocurrent”) when illuminated by either UV light or visible light, but other metals only did so for UV light. Detailed measurements of this “photoelectric effect” established the following characteristics:
- For a given metal, there exists a definite cut-off frequency, ⌫0. Incident light with frequency below ⌫0 produces no photocurrent regardless of its intensity.
- For light with frequency ⌫ > ⌫0, the magnitude of the photocurrent produced is directly proportional to the intensity of the incident light.
- The maximum kinetic energy of the photoelectrons does not depend on the intensity of the light, but it is proportional to the frequency of the incident light.
These characteristics could not be explained by the classical description of light as a wave that continuously transmits energy in proportion to the intensity of the light. Explaining these observations required a different description for light, which was proposed in papers by Max Planck (1901) and Albert Einstein (1905).⁸ They proposed to describe light as consisting of discrete bundles of energy, rather than as a continuous stream of energy. The bundles, or “quanta”, of energy were named “photons”. Each photon carries an energy of E = h⌫, where h is Planck’s constant with units of energy times time. The name of this constant honors Planck because he was the first to use the idea of quanta to explain the blackbody radiation spectrum. Einstein then used it to explain the photoelectric effect as follows.
A photon of incident light transfers all of its energy to an electron in the metal. If that energy is sufficient, it can dislodge the electron from the metal, i.e., it does some amount of work, W, to overcome the potential energy binding the electron in the metal. Any excess energy goes into the kinetic energy of the ejected electron,

E = W +

1
2

mv²
Using the photon energy, E = h⌫, we get
1
2

mv² = h⌫ W.

Not every electron is in the same potential, so the work required to eject them varies and their resulting kinetic energy varies. However, there is a minimum amount of work required for the most loosely bound

8The quantum explanation for the photoelectric effect is described concisely in a three page section of Einstein’s paper, Ann. Physik 17, 132 (1905), and was the reason for his subsequently being awarded the Nobel Prize.

electrons, which corresponds to a maximum kinetic energy for the ejected electrons. We can measure that maximum kinetic energy by applying a “stopping voltage” that photoelectrons must overcome to be detected. If we call Vs the voltage required to stop the most energetic electrons (and all the other electrons as well, of course), then eVs = 1
2mv²

max. Putting this all together we get the expression

Vs = h⌫/e | (13)

where is called the “work function” of the metal and corresponds to the minumum work required to eject an electron from that particular type of metal. Since we divided through by e, the work function has units of volts.
Equation (13) is a straight line on a graph of Vs(⌫), with a slope of h/e and a y-intercept of . By measuring Vs for different frequencies of light and fitting such a line we can determine both Planck’s constant and the metal’s work function.

### 4.1.1 Apparatus

The apparatus that we will use is shown in Fig. 13. It consists of a mercury discharge lamp that is the light source; a set of filters that transmit only a narrow range of wavelengths from that light and a special kind of vacuum tube called a phototube. The phototube has a cathode, from which a photocurrent will be produced, and an anode that will collect and measure the photocurrent, as well as provide an adjustable stopping voltage to impede the current. Using different filters allows you to change the ⌫ of the light. For each filter you can then adjust the anode-cathode voltage and find the value, Vs, that stops all photoelectrons from reaching the anode. Finding that value requires measuring the photocurrent that flows between the cathode and the anode in the vacuum tube; you can do that with the “electrometer”, which is a sensitive ammeter that can measure down to the picoampere range (1 pA = 1012 A). A voltmeter is also provided to measure the impeding voltage applied between the anode and cathode. A diagram of the circuit you’ll use for that is shown in Fig. 14, along with a more detailed view of the phototube.

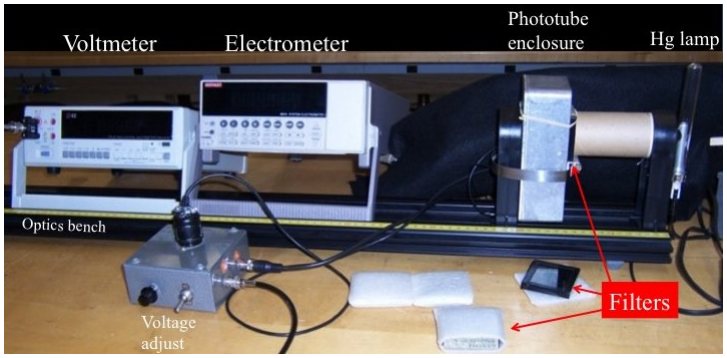
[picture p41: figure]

Figure 13: Photo of the apparatus mounted on an optics bench.

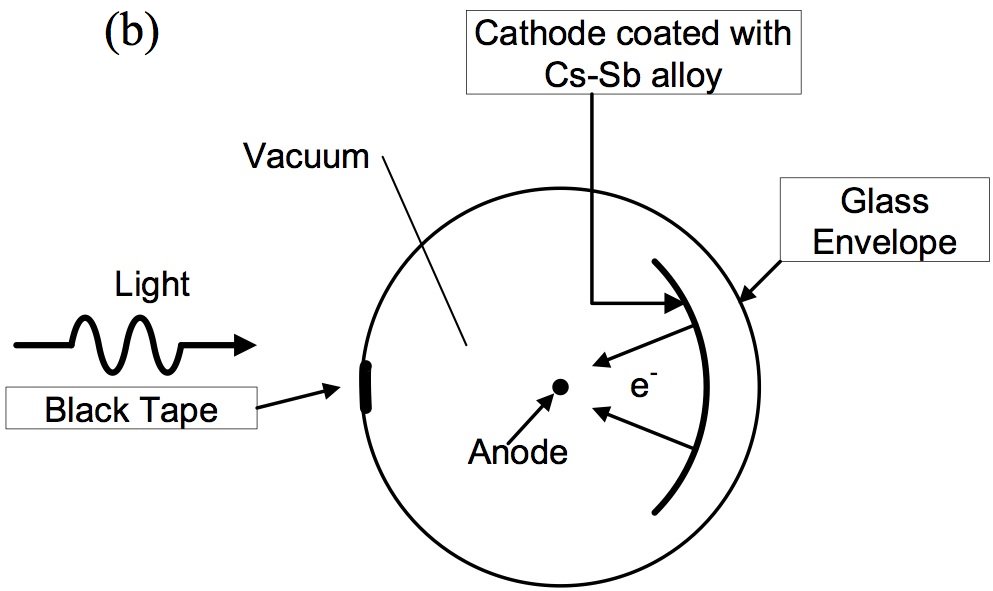
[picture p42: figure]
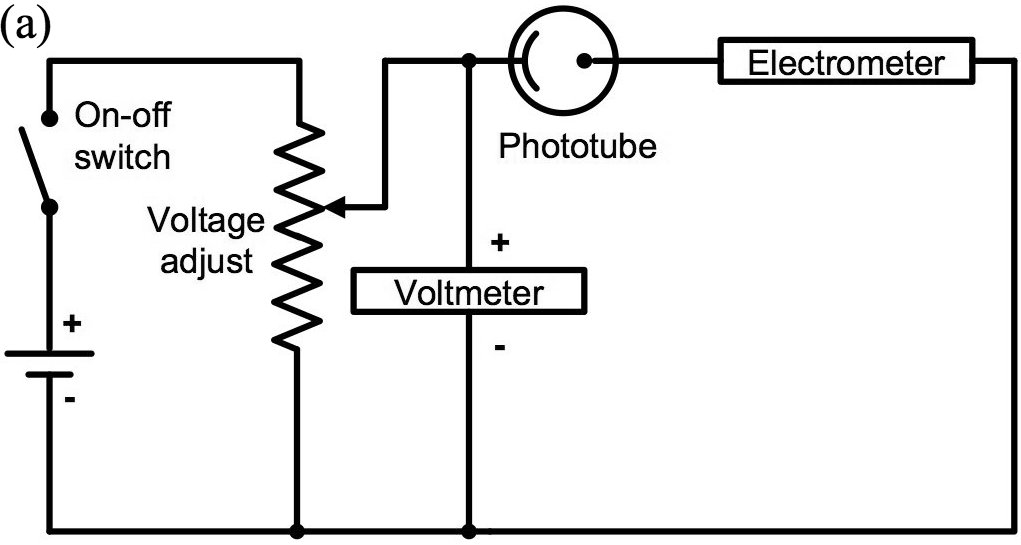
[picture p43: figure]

Figure 14: (a) Diagram of the circuit used in the experiment. An adjustable voltage divider controls the impeding voltage. Notice how the voltmeter and electrometer are connected in parallel and in series with the phototube, respectively. (b) Schematic of the phototube

Light enters the phototube and strikes the cathode, which is a metal plate coated with a Cesium-Antimony alloy. That alloy is chosen so that photoelectrons can be ejected from it by a range of visible light wavelengths without having to rely on UV light, which involves hazards worth avoiding. A small fraction of the photoelectrons ejected from the cathode will be directed toward and hit the anode. They’ll generate a photocurrent that runs through the electrometer back to the cathode. (The phototube thus converts photons into an electric current, just like a solar cell does, but it is very inefficient.) The battery and an adjustable voltage divider in Fig. 14(a) apply a voltage between the anode and cathode that impedes the natural flow of the photocurrent. The applied voltage pushes the electrons back from the anode to the cathode, so only electrons with sufficient kinetic energy to overcome the eV potential from the battery can reach the anode and flow through the electrometer back to the cathode.
Note that Fig. 14(b) shows a piece of black tape situated in the light path so as to keep the anode in its shadow. Think about why that is necessary, and write a brief explanation in your logbook.
The phototube is evacuated. Think about why it is important to have a vacuum between the cathode and anode, and write a brief explanation in your logbook.

### 4.1.2 Safety

The Hg lamp presents two hazards.
- It generates a spectrum of light that extends beyond the visible range into the ultraviolet. Prolonged exposure to ultraviolet emissions is hazardous to your eyes and skin. A glass test tube placed over the lamp is a simple way to shield yourself from the ultraviolet component of the lamp’s emissions because most glass is opaque at ultraviolet wavelengths. Before turning on the Hg lamp, make sure that the test tube shield is in place. Note also that the test tube has a white marking on it. This is normally used for labeling the contents. In our application is it not useful and could even be problematic if it blocks the light path. Keep the test tube rotated so that this white mark is out of the way of the light path.
- It gets hot. Don’t touch the lamp or test tube after it has been turned on, and keep any other materials away from contact with it.
You’ll want to make sure that the lamp is properly situated and turn it on at the beginning of the lab.

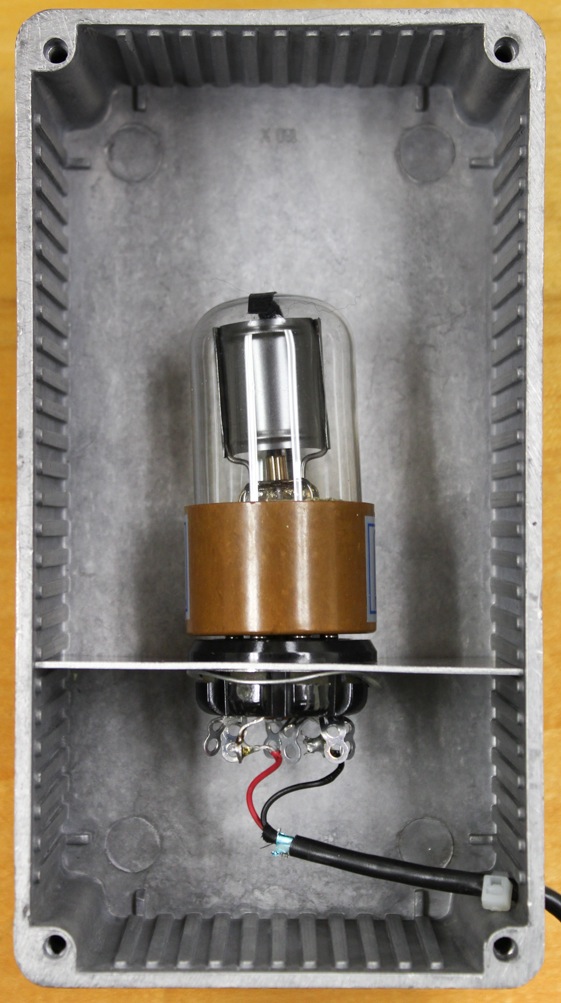
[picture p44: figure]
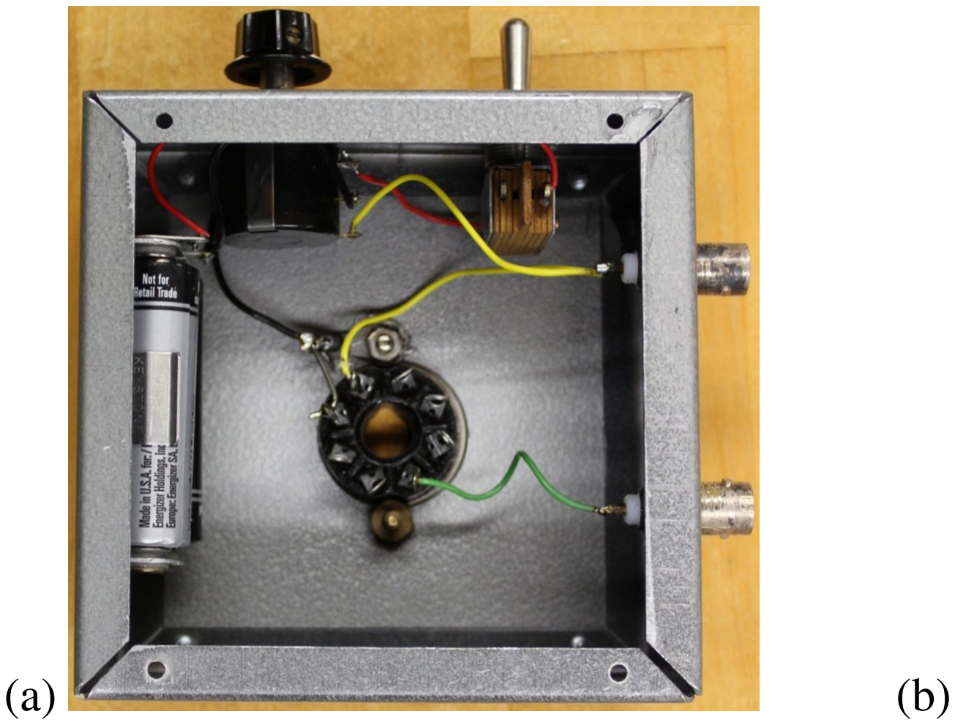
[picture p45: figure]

Figure 15: Photographs of the contents of the aluminum boxes containing (a) the voltage adjustment circuit and (b) the phototube.

Then leave it on and untouched. That way it will warm up and its output will remain more stable.
The phototube is enclosed in an aluminum box that has a small window to admit the incident light. This prevents ambient light, which has not been carefully wavelength selected by the filter, from affecting the measured photocurrent. Similarly, a short cardboard tube is used to block ambient light from entering the optical path between the filter and the light source. It also serves to keep your hands away from the hot lamp while swapping the filters. The battery and adjustable voltage divider are placed in another aluminum box with connectors for the voltmeter, electrometer and phototube. You won’t need to open either of these boxes, and you shouldn’t. To satisfy your curiosity, however, photos of their contents are shown in Figure 15.

### 4.2 Getting started and gaining familiarity

The first thing you should do in lab is turn on the meters so that they have time to warm up. Most equipment has a “warm up” period, which is simply the time it takes for all the heat production and dissipation mechanisms to come to equilibrium so that the device’s components remain at a constant temperature. Variations in temperature can alter operational details of electronics, such as amplifier gains and leakage currents. The electrometer has calibration circuitry that measures and corrects for most of these temperature dependent effects, but operating at a stable temperature still improves its precision. After re-reading the safety section... turn on the mercury lamp. Use a black cloth to make a tent over the lamp and metal enclosure, but make sure that the cloth does not touch the hot lamp.
Before taking data, spend some time to be sure you understand how the equipment works and take some more time to document its configuration. Take a photo of your setup and add it your logbook. Don’t use the photo in Fig. 13 because it is not your setup. Taking photos is one way to record views of your equipment from which you can later extract any details (e.g., make, model, size, position) that might be needed. You should also make a diagram of your circuit setup and put it in your logbook. It should look like the diagram in Fig. 14, but you should trace the connections in your setup just to be sure.

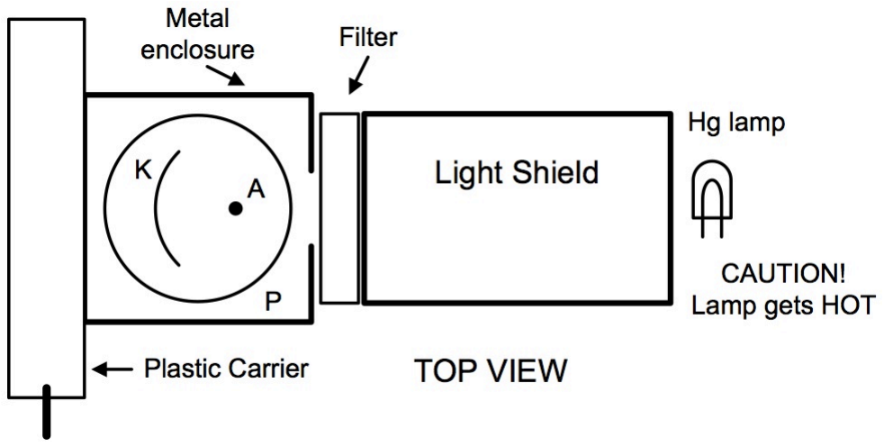
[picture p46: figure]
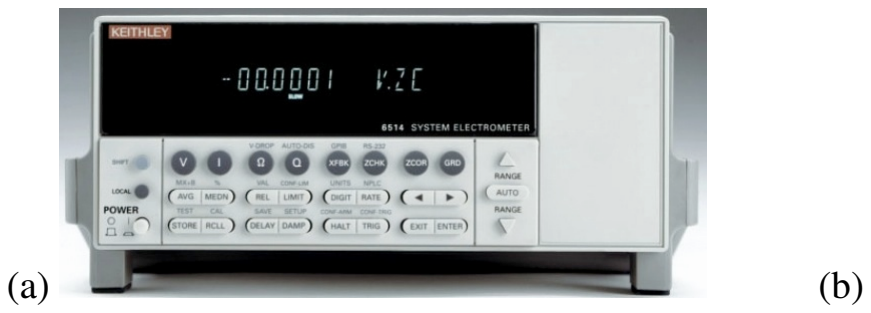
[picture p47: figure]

Figure 16: (a) Front panel of the Keithley 6514 Electrometer. (b) Diagram showing where to position the filter between the lamp and the phototube assembly.

### 4.2.1 Operation of the electrometer

The electrometer (Fig. 16) is central to your measurement, so you should understand its operation. You can find full details by googling for the equipment manual; what follows is excerpted from it.
The Keithley 6514 electrometer can be used to measure voltage, current, resistance or charge. We will only use the current measurement capability. When powered on, it defaults to voltage measurement mode. You can switch to current mode using the front panel button, but you should put the device into Zero Check mode (see below) when switching modes. It has ten ranges for current measurement, with the full scale values varying 20 pA to 20 mA. You’ll need to select an appropriate range for each of your measurements, or use the autoscale feature. For our measurements, the nA scale is probably optimal. The electrometer is capable of precision measurements of very small currents, but that precision requires some careful procedures. In particular, you need to calibrate and correct for any offset currents. This can be done with the Zero Check and Zero Correct functions. When Zero Check is enabled, the input signal is shorted so that the input amplifier sees only offset currents and voltages that are not from the input signal and thus should be subtracted. That subtraction can, and should, be done internally using the Zero Correct function, following the procedure listed in Fig. 17. It is reasonable to perform the zero correction procedure between each set of measurements (e.g., for each new filter) to compensate for any drifts that may occur over time.
You should also set the RATE setting to SLOW and the DIGIT setting to display 2 or 3 digits after the decimal point. Displaying more digits provides greater precision, but the temporal variation of the measurements is likely to be what will determine the uncertainty on your current measurements.

Zero Correction procedure to remove offsets
- Enable Zero Check mode. Press ZCHK; you should see a “ZC” message appear at the right side of the display.
- Select the current measuring mode by pressing I (if not already in that mode).
- Select the appropriate measurement range.
- Perform a zero correction by pressing ZCOR; you should see a “ZZ” message appear in the display.
- Press ZCHK to disable the Zero Check mode; you should now see a “CZ” message appear in the display to indicate that the subsequent readings are corrected for any zero point offsets.
Figure 17: Zero correction procedure.

### 4.3 Measure Vs(⌫) and extract h

There are four optical filters which only pass light in a narrow range of frequency. By placing these different filters between the Hg lamp and the phototube, you can make measurements of the phototube’s response as a function of the frequency, ⌫. A filter can be mounted on the small shelf that is attached to the phototube’s mounting box and held in place by a rubber band, as shown in Fig. 13. The filters vary in thickness, so you will have to adjust the space between the cardboard light shield and metal enclosure so that the light shield is touching the filter. Make this adjustment by sliding only the plastic carrier holding the metal enclosure; do not move the carrier holding the lamp. After mounting each filter, cover the lamp and phototube box with a tent made from the black cloth to minimize the effects of ambient light.
With a filter in place, you can measure Vs by adjusting the impeding voltage until the photocurrent reaches zero; the impeding voltage that stops all the current is the stopping voltage Vs. To make a reliable measurement of Vs, you should measure the photocurrent, I, as a function of the impeding voltage, V , and fit the data to obtain Vs. Taking a quick, coarse scan will give you an idea of the overall shape of I(V ). You can then decide on a set of voltages that seem appropriate and record a table of measurements in your logbook. Plot each of the I(V ) curves you measure and fit them for Vs. Make sure to put these plots in your logbook (and make sure they have proper labels on the axes, error bars on the points, the fitted function and its parameters).
After you obtain the Vs for each value of ⌫, fit that data to Equation (13) to obtain h/e and . This plot is the key result. While Planck’s constant is the main result, the fit will also determine the metal’s work function, which is also an interesting, though less fundamental, parameter.
Although the lab period does not have sufficient time for a thorough exploration of systematic uncertainties in the measurement, you should spend a few minutes thinking about what possible effects might have systematically biased your measurement and what auxiliary measurement you might make to measure these effects.
You can compare your measured value to the most precise measurement currently available, from NIST, of h = (6.62606957±0.00000029)⇥1034 J s. However, don’t let your thought process be biased by how close or far your measurement is from that value. You should approach your measurements as if you were the first to have ever measured this value!
Finally, write your conclusion. It should include a statement of what you did, how you did it, what you measured, the uncertainty in your measurement and what the main contributions to your uncertainty were.

### 4.4 Going Beyond

There are several ways that exceptional students could improve the precision and robustness of this measurement. A few ideas are listed below, but I encourage you to use your own creativity.
- Repeat the Vs measurements with at least some of the filters. If the results differ significantly from your first set of measurements, you have evidence for a systematic uncertainty, and you have a measurement of that uncertainty, which should be included in your final determination of h.
- It would be best to electronically record the currents and voltages to obtain a fine grained I(V ) curve. The electrometer has a computer interface that would allow this, but using it requires a lot of setup. Can you think of another, simpler way to record both I and V as fine grained raw data that you could subsequently extract for an I(V ) plot with many data points?
- Talk to your classmates and collect their measured values. With all of that data, you could do a global analysis of Vs(⌫) that would let you both understand any systematic uncertainties and obtain a more precise determination of h.
- We relied on the advertised wavelength range for the filters. Can you think of a way to measure the filters’ wavelength range yourself? Even if you don’t have time to do so, it is interesting to think through and write out a plan for how you might carry it out in lab.

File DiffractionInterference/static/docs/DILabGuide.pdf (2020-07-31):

# Physics 25L lab manual

### Professor Deborah K Fygenson, UCSB Physics Department

This is a modified version of the original manual written by Professor David Stuart

### April 5, 2019

## Contents

1 Introduction to Experimental Methods | 3
1.1 Uncertainties | | 3
1.1.1 Estimating uncertainties | | 4
1.1.2 Propagating uncertainties | | 6
1.1.3 Plotting and fitting | | 7
1.2 Validation of results | 10
1.3 Rigorous record keeping | 12
1.4 Excelling | 14
2 Gamma ray absorption | 16
2.1 Pre-lab preparation | 16
2.1.1 Interaction of radiation with matter | 17
2.1.2 Apparatus | 18
2.1.3 Safety and care of equipment | 20
2.2 Getting started and gaining familiarity | 20
2.3 Measuring the mass absorption length | 21
2.4 Data analysis | 22
2.4.1 Beware biases | 24
2.4.2 A concise summary of results | 25
2.5 Going Beyond | 26
3 Interference and Diffraction | 27
3.1 Pre-lab preparation | 27
3.1.1 Experimental planning | 30
3.1.2 Apparatus | 31
3.1.3 Safety | 32
3.2 Getting started and gaining familiarity | 32
3.3 Qualitative observations of interference and diffraction | 32
3.4 Measurement of the wavelength of a laser | 32
3.4.1 Image analysis | 34
3.4.2 Putting it all in your logbook | 34
3.5 Going beyond | 35
4 The Photoelectric Effect, Photons and Planck’s constant | 36
4.1 Pre-lab preparation | 36
4.1.1 Apparatus | 37
4.1.2 Safety | 38
4.2 Getting started and gaining familiarity | 39
4.2.1 Operation of the electrometer | 40
4.3 Measure Vs(⌫) and extract h | 41
4.4 Going Beyond | 41
5 Atomic spectra and the Rydberg constant | 43
5.1 Pre-lab preparation | 43
5.1.1 Apparatus | 44

5.1.2 Safety and care of equipment | 46
5.2 Getting started and gaining familiarity | 46
5.3 Measuring the spectrum and extracting Rydberg’s constant | 47
5.4 Measuring the spectrum of an unknown source | 48
5.5 Going Beyond | 48
6 The Franck-Hertz experiment | 77
6.1 Pre-lab preparation | 77
6.1.1 Apparatus | 78
6.1.2 Safety and care of equipment | 78
6.2 Getting started and gaining familiarity | 78
6.3 Measuring the excitation energy | 79
6.4 Going Beyond | 79

## 3 Interference and Diffraction

Abstract: In this lab, you will observe the effects of diffraction of visible light through a narrow slit and of interference of light passing through multiple slits. You will use the interference patterns to measure the wavelength of the light from a laser.

### 3.1 Pre-lab preparation

Interference is a property of waves. Put simply, waves superimpose - meaning that the amplitude at any position and time is the sum of all waves at that position at that time. If the superimposing waves are periodic and coherent, they combine in ways that lead to striking phenomena: standing waves on a string (discussed in Phys 23), diffraction of water waves around a corner, and interference of sound waves from a pair of speakers (discussed in Phys 24). In this lab, we will examine diffraction and interference more closely using light waves, and then use these phenomena to measure the wavelength of the light from a laser.
Consider two point sources of light that are completely coherent (i.e., they emit light of the same intensity and wavelength, and do so in phase with each other). The light from each point source propagates in all directions, but for simplicity we will consider only a single plane. Suppose these point sources are separated by a distance d. We’ll use the (x, y) plane and place the light sources at points (0, 0) and (0,d) (see Figure 9). We can then determine the intensity of the light at different points along a screen, placed a distance L away on the x-axis, by considering the superposition of the two light waves at an arbitrary point, (L, y), on the screen.

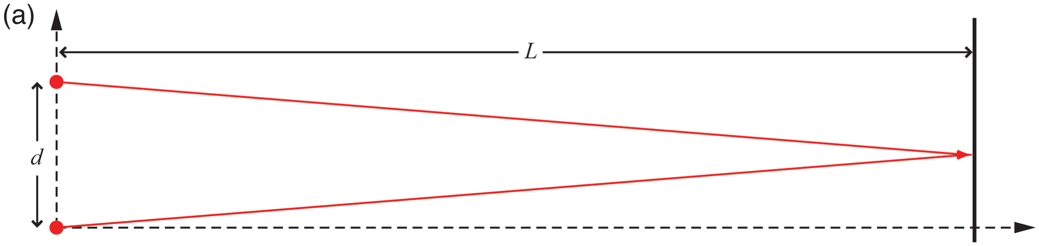
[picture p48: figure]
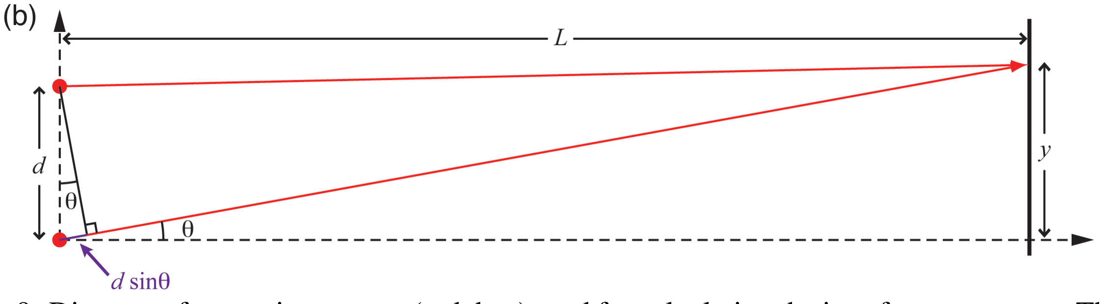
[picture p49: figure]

Figure 9: Diagram of two point sources (red dots) used for calculating the interference pattern. The (x, y) coordinate system is shown by the dashed lines. The point sources are separated by a distance d, and the interference pattern is calculated considering the light projected onto a screen a distance L away along the x axis. (a) Light rays of equal pathlength reaching a point on the screen; because they traveled the same distance, the light from the two sources are in phase with each other and constructive interference occurs. (b) Light rays reach a point on the screen where their pathlengths differ by an amount d sin ✓, with consequences discussed in the text.

As shown in Figure 9(a), at the point (L, d/2), the path length for each of the two light waves is equal. That leaves the two waves in phase with each other, so they add (i.e., interfere) constructively, and make a bright spot at that point on the screen.
At any other point on the screen, the path lengths of the two light waves differ, as shown in Figure 9(b), where the light that comes from the lower point travels an additional length d sin ✓. This light arrives at the screen with a phase that is shifted by =2⇡d sin ✓/ with respect to the light from the upper point. If the additional path length d is such that d sin ✓ = /2 then the phase shift is = ⇡. That makes the wave from the lower point exactly the negative of the wave from the upper point, so they interfere destructively and that point on the screen is dark.
We can calculate the y-coordinate, y = L tan ✓, of the point on the screen where this destructive interference occurs. If ✓ is small (i.e., if L d), then we can approximate tan ✓ ⇡ sin ✓, so ydestr ⇡
L sin ✓ = L/2d.
Another special point on the screen, (L, yconstr), is where the path lengths of the two light waves differ by exactly one wavelength, i.e., d sin ✓ = . At this point, the phase of the light that travels the longer path is shifted with respect to that of the light that travels the shorter path by =2⇡d sin ✓/ =2⇡, which has the same effect as no phase shift at all, so the two waves interfere constructively. Mathematically, if yconstr = L sin ✓ = L/d, the point on the screen at (L, yconstr) will be bright.
The pattern repeats for larger values of y: destructive interference occurs at any point for which is an odd multiple of ⇡ and constructive interference occurs at any point where the phase difference is an even multiple of ⇡. The generalized relations for yconstr and ydestr are key to what you’ll do in this lab, so I’ll write them here in an easily findable and concise mathematical format These relations are key to what you’ll do in the lab, so I’ll rewrite them in an easily findable format:
ydestr = nL/2d, where n = ±1, ±3, ±5,... | (10)
yconstr = nL/d, where n =0, ±1, ±2, ±3,... | (11)
(The drawing in Fig. 9 includes a coordinate system offset of d/2, but this is negligible since we are working in the limit where L d.)
I suggest you start taking notes in your eLogbook for Week 2 by writing these equations and drawing a diagram that clearly defines the variables by yourself. Generate the equations in your eLogbook using the Google plug-in Auto-LaTeX Equations (https://chrome.google.com/webstore/detail/auto-latex-equations/iaainhiejkciadlhlodaajgbffkebdog?hl=en-US) so that they are neat and easy to read. Generate the diagram by hand and take a picture, or use a vector graphics app like Adobe Illustrator (https://www.adobe.com/products/illustrator.html) (powerful, but expensive), Affinity Designer (https://affinity.serif.com/en-us/designer/) (equally powerful, and not expensive, but not free), Inkscape (https://inkscape.org/) (free, but clunky), or Vectr (https://chrome.google.com/webstore/detail/vectr/ncpaehbhmfoodbceflpbdocjhpokkbmo?hl=en) (free and clunky, but works in your browser). Insert the result into your eLogbook. The act of generating the equations and diagram yourself is a good exercise in using LaTeX and vector graphics. Even if you are already facile with these tools, it can help you think through and really understand the math/physics. If you don’t need the practice with the tools, and you already understand the physics, go ahead and just copy and paste screenshots. Just having the equations and diagram in your notes will make them more useful in future reference. You want to learn to keep an eLogbook that is a standalone description of what you are planning, doing, observing and thinking. No one should have to have access to the Physics 25L lab manual to understand what you are doing and why.
In fact, it is a good idea to start writing in your eLogbook before you even go to lab. Write whatever helps you: notes on reading through the manual, questions that occur, ideas for how you might go beyond. Put enough in your notes (e.g., keywords, sketches, highlights, emojis) so that you can find what you need by scrolling through or searching.

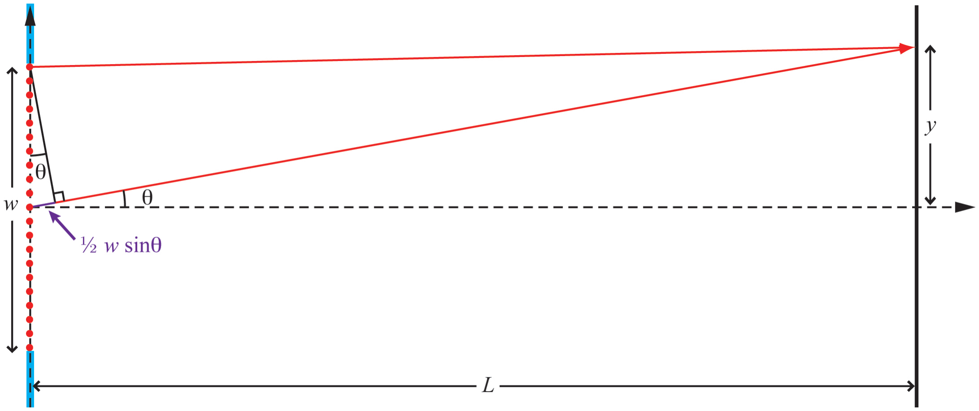
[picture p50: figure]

Figure 10: Diagram of multiple point sources (red dots) used for calculating the diffraction pattern of a thin slit. The blue lines are a material blocking all light except for the thin slit of width w, which is situated symmetrically across the y-axis. Interference of light from two points separated by w/2, one above and one below the y-axis, have pathlength difference of w

2 sin ✓ when reaching the screen placed at x = L, with consequences discussed in the text.

An experimentally direct way to create two coherent light sources is to shine a single laser on something opaque that has two very small holes poked in it. If the holes are small enough, they will each behave as a point source from which spherical light waves emanate. Because the incident laser light is coherent, the holes will be coherent light sources.
This is basically the approach that we’ll use in this lab, but we’ll use slits rather than holes. We are only looking in two dimensions, (x, y). A slit in the z-direction is the same as a hole for that purpose, with the added benefit that we can illuminate a slit without having to aim the laser as carefully!
A possible problem with this approach is that our slits are not necessarily narrow enough to be truly “point” sources in the plane. So, let’s consider the effect of passing light through a finite slit width. We’ll do that by considering a single slit of width w as shown in Fig. 10. We’ll again consider only the xy-plane, and following Huygen’s principle, we can consider the wavefront at the slit as a series of coherent point sources, illustrated by the red dots in the figure.
It is easy to see that there is constructive interference at the point (L, 0) because for every point source in the slit, at a position of say (0,y1), there is another point source at (0, y1), symmetrically across the y-axis, which therefore has the same pathlength to the point (L, 0). As a result, there is constructive interference, and hence a bright spot, at (L, 0).
Using a similar argument, we can see that destructive interference will occur at some point (L, ydestr). This happens because light from the point at (0, w/2) and light from the point at (0, 0) have a pathlength difference of (w/2) sin ✓. If that pathlength difference equals /2, then the light rays will combine out of phase and destructively interfere.⁶ Given that the light from the point (0, w/2) is canceled by the light from (0, 0), it follows that light from the point (0, w/2 ) is canceled by light from (0, ). In fact, at ydestr = L/w, the light from any point in the upper half of the slit is canceled by a point that lies a

6Note that, when solving for ydestr = L/w, the two factors of 1/2 cancel and the “small angle approximation” allows us
to set tan ✓ ⇡ sin ✓.

distance w/2 below it, in the lower half of the slit. As a result, all of the light from the slit undergoes destructive interference at the point (L, ydestr); the point appears dark. The same argument applies for any point with a y-coordinate that is an odd integer multiple of /2, so there are dark spots for

ydestr = nL/w, where n = ±1, ±2, ±3, ... | (12)

This is called a diffraction pattern; it is a special type of interference pattern that results from light passing through different parts of a finite width slit. The light is said to “diffract” through the slit. (Notice that as the slit width w goes to zero, the point of destructive interference moves out to infinity along the y-aixs and we get the spherical wave pattern of a single point. In the opposite extreme, as w goes to infinity, the spacing between dark points goes to zero so no pattern is discernible.)
In this lab, you will look at both the diffraction pattern from a single slit and the interference pattern from two, or more, slits. The pattern from two slits will be a convolution of the interference pattern from the two slits and the diffraction from each slit. A typical two-slit pattern is sketched in Figure 11. The number of interference maxima within each diffraction peak depends on the ratio of the slit width to the slit spacing, so the pattern you observe may be substantially different in this respect.

Figure 11: Cartoon of the pattern expected from two thin slits. The diffraction pattern (dashed line), defined by the slit width, is convolved with the interference pattern, defined by the slit spacing, to give the intensity vs position shown by the solid line.

### 3.1.1 Experimental planning

In this lab you will observe the qualitative features of interference and diffraction patterns and then use them to measure the wavelength of the laser. Since the wavelength of visible light is less than a micron, you will need to use some clever experimental “tricks” to extract a precision measurement.
The first trick will be to leverage the fact that an interference pattern scales with the wavelength times L/d. You will use small slit spacings, d, and a long optical path, L, to make the pattern visible. Even so, the pattern will still only be a few centimeters across. How might you precisely measure the positions of the maxima and minima? Think for a minute or two before reading further to see if you can come up with an idea.
The next trick will be to make a precise measurement of the distance between the slits. The apparatus provided will specify the width and spacing for each set of slits. The available slit-widths range between 0.02 mm and 0.16 mm, and the slit-spacings range from 0.25 to 0.5 mm. (You could just use the advertised sizes, but for a serious measurement you don’t want to simply trust what the sales department says! You should measure it yourself!) How might you measure these small distances with precision of 10% or better? Again, think a bit and come up with your own ideas for this before reading further. Go ahead and write your thoughts in your eLogbook, while you’re at it!

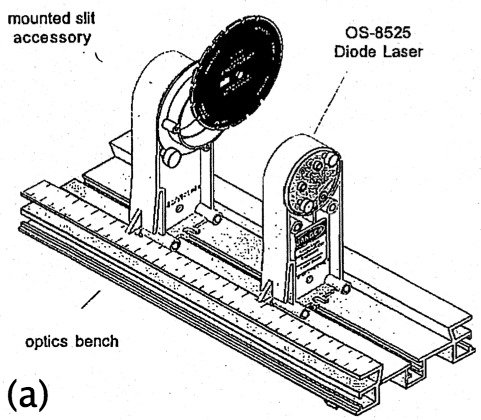
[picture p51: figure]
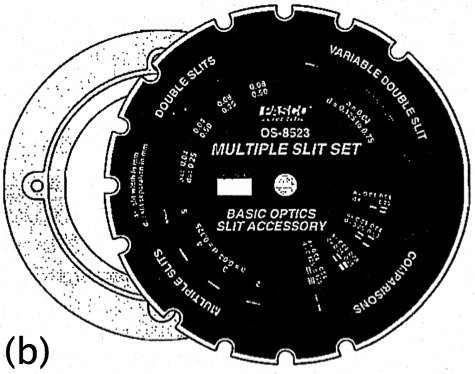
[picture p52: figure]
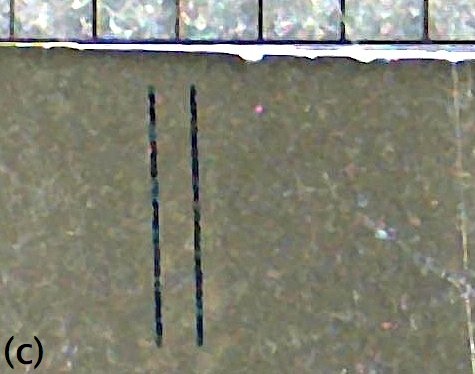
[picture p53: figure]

Figure 12: (a) The PASCO OS-8515 Basic Optics System with a OS-8525 Laser Diode assembly and OS-8523 slit accessory mounted. (b) A close-up of the Multiple Slit Accessory. There is a similar Single Slit Accessory; each accessory allows you to change which slit (or set of slits) is in the laser beam by rotating part of the device. (c) A close-up of one pair of slits, taken through a microscope; a ruler with 1 mm divisions is placed at the top of the field of view to calibrate the scale.

### 3.1.2 Apparatus

The apparatus you will use is an optics bench with a movable laser mount, a movable slit mount and a movable screen mount, as shown in Fig. 12(a). The “bench” provides a robust way to set and measure the positions of each of the movable mounts.
Measuring positions of maxima and minima: One way to measure the positions of maxima and minima in the interference pattern is to take a photo of the pattern with a ruler placed in the field of view. You can then use image analysis software to measure the spacing of the maxima and minima in units of pixels within the image and scale that by the number of pixels per mm using the ruler. Ruled graph paper works just as well as a ruler, and can be easier to attach to the screen, but make sure the light pattern itself falls on a blank (i.e., unruled) background so that the rulings don’t impose intensity variations on top of the pattern you are trying to measure. (Attach a piece of graph paper or a ruler to the screen with clips; don’t write directly on the screen.)
Your cell phone is a convenient tool for taking the photos. You can use your own laptop or the computers in the lab to view, process and analyze your image data. The computers in the lab have a powerful image analysis software installed called Fiji. (https://imagej.net/Fiji/Downloads) This free software is developed and maintained by the National Institutes of Health and works on Macs as well as PCs. If you are already familiar with a different image processing software, feel free to use that instead.
Measuring the slit width and spacing: You can also make a precise measurement of the slit width and spacing with a camera and image processing, if you have enough zoom in your camera. But, even then you’d have a hard time holding the camera still enough to get a well focussed image. So, we have a couple USB microscopes that will serve the same purpose. They’re basically a webcam with microscope optics attached. They have enough magnification to resolve the slits with a reasonably large number of pixels. So, you can get an image with a length scale (ruler) within the image, and process the image as discussed above. Note that the magnification and resolution is probably insufficient to measure the slit width. However, the spacing can be measured reasonably well, and that is the important independent variable for an interference pattern.

### 3.1.3 Safety

The lasers you will use in this lab are not high power, but they can still impair or permanently destroy your vision if the beam strikes your eye directly. A few safety precautions are appropriate:
- Do not look directly into the laser beam.
- Use caution when adjusting the optics to avoid accidentally reflecting the laser toward your, or anyone else’s, eyes.

### 3.2 Getting started and gaining familiarity

The first thing you should do in lab is play around with the optics bench to understand how it works. Slide the mounts around, and set up your screen. If you like, take a photo of the setup with your cell phone for your logbook. You don’t need to immediately insert the photo into your eLogbook, but it is a good habit to note the time you took it. Alternatively, you could draw a schematic your setup. Honestly, a schematic is often a lot more useful. Photos capture tons of information that can obscure, or just distract from, the essential. A schematic captures only what you want it to and is easily labeled. Either way, you should note the make and model of the various components in your setup as best you can.

### 3.3 Qualitative observations of interference and diffraction

Use the Single Slit Accessory, view the diffraction pattern using at least three different slit widths. Take photos of the patterns for your logbook. Write your name, the slit width and any other variables that you suspect effect the pattern on a post-it note and include that writing in the photograph’s field of view. In general, it is a good habit to include such “metadata” directly in your experimental data whenever possible because doing so can resolve ambiguities that might arise later on down the line.
Write a brief qualitative summary of your observations. For example, you might conclude that the separation of the maxima and minima increases as the slit width decreases. Of course, that is what you expect from equation (12), but the point of doing an experiment is to record what you observe in a clear and concise way. Imagine that the theory of the diffraction pattern where not yet understood, and write your conclusions with the intention of defining the experimental facts that a developing theory must explain.

### 3.4 Measurement of the wavelength of a laser

The observations you just completed were a qualitative way to get familiar with the phenomenon of interference. Now, it’s time to make a measurement. Your goal is to measure the laser’s wavelength as precisely as possible. You will do this using the the Multiple Slit Accessory and the relations in equations (10) and (11), where you can measure L, y, and d and extract .
Start by thinking about the uncertainties. In your logbook, calculate how the uncertainty on depends on the uncertainties in the things you will measure. Then make some estimates. What do you think the uncertainties will be in each of the three parameters, i.e., L, y, and d? Which of the three do you expect to dominate the total uncertainty in ?

Recall from section 3.1.1 that you should measure d, not just take the advertised values for granted. We have a couple USB microscopes available as well as some zoom lenses that you can fit over your cell phone’s camera. You’ll want to take several different photos and obtain multiple measurements. Averaging these measurements gives you a more precise result, and looking at the root-mean-squared deviation (RMS) of the measurements helps you determine a valid uncertainty. You can make the slit measurement at the beginning or end of the interference pattern measurements, however you prefer. Next, you should think about possible systematic errors. While the fractional uncertainty in L is probably going to be smaller than the other uncertainties, it is something that could easily have a systematic bias. For example, while the optics bench provides a nice way to measure the position of the little tab that sticks off the side of the mounts, that isn’t necessarily the position of the slit or the screen. The difference between those two positions will be a systematic bias on L.
There is, however, a trick to avoid that systematic uncertainty in L: measure y as a function of L and fit the results to a straight line. The slope of that line gives (after correcting for d). The systematic uncertainty from the difference between the mount’s position and the actual slit position changes the intercept of the line, but not its slope. Measuring the dependence of two observables and extracting a desired quantity from a fit is a common trick because of its ability to do away with certain systematic errors, and because it is a very good way to validate the data. For example, the goodness of the fit (the ² per degrees of freedom) shows whether the measurements are behaving properly within the determined uncertainties. If the ² is too small, the uncertainties may be overestimated. If the ² is too big, either the uncertainties are underestimated or there is something else going on beyond what is assumed in the model (i.e., the equation to which the data is being fit).
You should make measurements for several different values of L and use a fit to extract . As discussed in section 3.1.2, you can obtain a more precise measurement of the positions of the maxima and minima by photographing the pattern and using image analysis software to determine the positions in pixels, and calibrating pixels to distance. Think a bit about how you will do this. Write your thoughts in your notes.
It is, in general, a good idea to plan your experimental protocol before you begin. Here are some tips that might help you plan:
- Make a table in your logbook where you record information about each measurement. It should include a unique identifier for each measurement (e.g., a number, letter, or combination thereof).
- Write that identifier on a piece of paper that you can attach to the screen so it is visible in the photos as metadata.
- Note the filename (or equally identifying information) for each photo in your logbook. (You need not print out and tape in these photos, but you should save the files somewhere you will be able to find at some far future time when you might need to revisit this.)
- Take more than one photo for each value of L. This will allow you to select the best one, e.g., if some have focus, lighting or perspective problems. It will also allow you to compare the measured y values between two or more good photos to assess whether the uncertainties are as you estimate.
- It is more precise to measure the difference between the +1 and -1 maxima and then divide by two than it is to just measure the difference between +1 and 0. Similarly, you might find it more precise to determine the position of the minima than the maxima.
- Leave enough space in your table to add comments or other information later.

- Using a larger number of slits gives narrower, more sharply defined maxima.
Once you have thought through your plan, summarize what you have decided to do and why in your logbook. Now you are ready to start taking data. (Of course, your actual procedure may differ from your plan as have ideas, make mistakes, gather new information. If it does, just note how and why - you don’t have to re-write the whole plan unless you want to (e.g., to make it easier to reconstruct later). As President Eisenhower famously said, ”Plans are useless, but planning is essential!”
Ideally you would analyze each photo as you take it, but given your limited time with the equipment, doing so would not allow you to make enough measurements to get good precision. Still, you should promptly analyze at least the first photo, i.e., copy it into your image processing software and extract a distance to make sure the photo has all the qualities that will make it easy to analyze. This is a good habit because it is best to find problems at the beginning rather than after you’ve spent 30 minutes collecting data.

### 3.4.1 Image analysis

You are free to choose whatever method you prefer to measure the positions in your images. As mentioned above, I recommend the NIH ImageJ-based package called Fiji (https://imagej.net/Fiji/Downloads) because it is platform independent, has an intuitive user interface, a complete suite of tools, and good documentation. (https://imagej.net/Introduction) I encourage you to download it onto your own computer so you can play around with it any time. It is also available on the computers in the Physics 25L lab room.
Within Fiji you can draw a line anywhere on your image, in any direction, and of any thickness (double-click on the line-selection tool in the toolbar to set the thickness, a.k.a. line width) Once you’ve drawn a line, you can use Analyze i Plot Profile to create a plot of intensity values (averaged
across the width of the line) versus position along the length of the line. Pushing the | List | button gives
a list of the intensity values used to create the plot. These values can be copied and pasted into your favorite graphing program for further plotting and fitting. Read more about this and other commands available in the Analyze menu in the on-line documentation. (https://imagej.nih.gov/ij/docs/menus/analyze.html)
Feel free to brainstorm with your classmates about how to best get at the information you want. If you get a particularly good idea from a classmate, feel free to use it for your measurement, but you should cite them in your logbook as the source of the idea.

### 3.4.2 Putting it all in your logbook

Whatever analysis method you use, the goal is to obtain a set of measured ydestr or yconstr values. These should go into a table in your logbook. And you should make plots of them (e.g., ydestr vs L with a linear fit). Paste the plots into your logbook.
Finally, make sure that your logbook has a clear and concise conclusion. It should state the qualitative features you observed and the wavelength value that you measured complete with uncertainty in your measurement.

### 3.5 Going beyond

There are several opportunities for you to go beyond the minimal requirements, and I encourage you to do so. This class will prepare you for an experimental research position or internship and ultimately for experimental research in graduate school. I’m often asked by students of lab courses to write letters of recommendation for their graduate school applications. Saying that they did everything required of them is underwhelming, but it is great when I can point out where they have pursued additional ideas and/or tried their own methods. Make doing so your habit.
Here are a few additional things you could measure or explore if time allows.
- Measure the positions of the minima in the photos of your single slit diffraction patterns and plot them vs the slit width. Does it fit to 1/w?
- Measure the spacing between the first, the second, and (maybe) the third minima in either the diffraction or the interference patterns. Are they equal?
- Observe the patterns from other features on the Single Slit Accessory, e.g., there is an opaque line that can be compared to a transparent slit.
- A CD or DVD consists of circular tracks with a small spacing. Light passing through (or reflecting from) those tracks will generate an interference pattern. Now that you know the wavelength of your laser, determine the track spacing for a CD or DVD.
- Measure the thickness of your hair.

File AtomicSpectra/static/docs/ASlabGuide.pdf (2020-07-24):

# Physics 25L lab manual

### Professor Deborah K Fygenson, UCSB Physics Department

This is a modified version of the original manual written by Professor David Stuart

### May 9, 2020

## Contents

1 Introduction to Experimental Methods | 3
1.1 Uncertainties | | 3
1.1.1 Estimating uncertainties | | 4
1.1.2 Propagating uncertainties | | 6
1.1.3 Plotting and fitting | | 7
1.2 Validation of results | 10
1.3 Rigorous record keeping | 12
1.4 Excelling | 14
2 Gamma ray absorption | 16
2.1 Pre-lab preparation | 16
2.1.1 Interaction of radiation with matter | 17
2.1.2 Apparatus | 18
2.1.3 Safety and care of equipment | 20
2.2 Getting started and gaining familiarity | 20
2.3 Measuring the mass absorption length | 21
2.4 Data analysis | 22
2.4.1 Beware biases | 24
2.4.2 A concise summary of results | 25
2.5 Going Beyond | 26
3 Interference and Diffraction | 27
3.1 Pre-lab preparation | 27
3.1.1 Experimental planning | 30
3.1.2 Apparatus | 31
3.1.3 Safety | 32
3.2 Getting started and gaining familiarity | 32
3.3 Qualitative observations of interference and diffraction | 32
3.4 Measurement of the wavelength of a laser | 32
3.4.1 Image analysis | 34
3.4.2 Putting it all in your logbook | 34
3.5 Going beyond | 34
4 The Photoelectric Effect, Photons and Planck’s constant | 36
4.1 Pre-lab preparation | 36
4.1.1 Apparatus | 37
4.1.2 Safety | 38
4.2 Getting started and gaining familiarity | 39
4.2.1 Operation of the electrometer | 40
4.3 Measure Vs(⌫) and extract h | 41
4.4 Going Beyond | 41
5 Atomic spectra and the Rydberg constant | 43
5.1 Pre-lab preparation | 43
5.1.1 Apparatus | 44

5.1.2 Safety and care of equipment | 46
5.2 Getting started and gaining familiarity | 46
5.3 Measuring the spectrum and extracting Rydberg’s constant | 47
5.4 Measuring the spectrum of an unknown source | 47
5.5 Going Beyond | 48
6 The Franck-Hertz experiment | 78
6.1 Pre-lab preparation | 78
6.1.1 Apparatus | 79
6.1.2 Safety and care of equipment | 80
6.2 Getting started and gaining familiarity | 80
6.3 Measuring the excitation energy | 81
6.4 Going Beyond | 82

## 5 Atomic spectra and the Rydberg constant

Abstract: In this lab you will observe the visible spectrum of Hydrogen and use it to measure the Rydberg constant. Then you will use the spectrum of an unknown source to determine its atomic content.

### 5.1 Pre-lab preparation

The quantum explanation for atomic structure was developed in the early 1900’s, based largely on the evidence for quantized energy levels of atoms that was accumulated in the late 1800’s through measurements of various atomic spectra. In 1885, Johann Balmer measured the visible spectrum of Hydrogen and found the wavelengths of light that were present were related according to

1
= R

✓ 1
2² 1
n²

◆
; for n> 2 . | (14)

The ultraviolet and infrared portions of the spectrum were later measured (by Lyman, Paschen, Brackett and Pfund) and found to fit into similar formulas but with integers other than 2 in the first term (and in the inequality). They all measured the same coefficient, R, called the Rydberg constant. The origin of this formula was eventually understood within the Bohr model of the atom. The light from Hydrogen consists of photons of energy E = h⌫ = hc/ that are emitted by atoms transitioning between electronic states that have discrete (quantized) energies of En = hcR/n², where n is a positive integer. (These energy levels are illustrated in Fig. 18.) This understanding allowed the Rydberg constant to be calculated as R = me⁴/8✏0h³c, whereas previously it had been only an empirically determined value.⁹

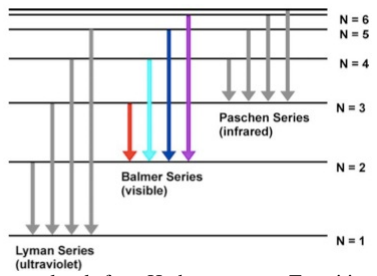
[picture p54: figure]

Figure 18: Diagram of the energy levels for a Hydrogen atom. Transitions between excited states down to the n =2 state produce visible light (red to violet, left to right for the four lines shown) that you will observe in this lab. Transitions to the n =1 state produce ultraviolet light, and those to the n =3 state produce infrared light, neither of which can be seen by eye.

In this lab, you will measure the visible spectrum of Hydrogen as Balmer originally did and, from it, obtain a measurement of the Rydberg constant.

9Interestingly, the measured value of R did not match the prediction of the simplest Bohr model which uses m = me because the electron and proton together lead to an effective “reduced mass”, m, that is very slightly below the electron mass. Furthermore, the spectrum of hydrogen was found to contain a set of wavelengths with a slightly different R value. These come from deuterium, which is hydrogen with a neutron in the nucleus, the mass of which further alters m). Both effects are smaller than 0.1% and only revealed by exquisitely precise measurements.

Equation (14) applies only to Hydrogen. Other atoms have a similar 1/n² structure in their spectra but with a different coefficient. Each element’s spectrum is uniquely characteristic, so spectra are often used to identify the elemental composition of a sample (or a star 10!). After you have completed your measurements on a Hydrogen sample, you will measure the spectrum of an unknown sample (or two!) and identify its elemental composition.

### 5.1.1 Apparatus

The apparatus you’ll use is called a spectroscope. It uses the phenomenon of interference, which you explored in the double slit experiment that you did two weeks ago, but instead of two slits, a spectroscope uses a diffraction grating with a very large number of equally spaced slits of identical width. Many equally spaced slits create a pattern with maxima at the same positions as in the pattern created by two slits with the same spacing, but when there are many slits, the maxima are much more narrowly peaked, (i.e., the contrast is much improved). Because of its very large number of slits, a diffraction grating creates very sharp maxima.
The diffraction grating you will use is made by etching thin parallel lines on a piece of glass. Etched regions scatter light instead of transmitting it, so the non-etched regions between the etched lines act as slits. The etching process allows hundreds or thousands of lines per mm, so this type of diffraction grating has slits that are not only plentiful, but closely spaced as well. Your diffraction grating should specify the number of lines per mm, from which you can calculate the spacing, d, between any pair of slits.
The close spacing puts a large lever arm on the pattern (i.e. a greater angular separation between maxima) making it possible to distinguish maxima of many different wavelengths. As you’ll recall, interference from slits separated by a distance d results in intensity maxima at angles ✓ for which d sin ✓ = m, where m is any positive integer. The m =0 case is the central maximum with no deflection (i.e., ✓ =0). By finding the ✓ values for the m = ±1 maxima for each of the different wavelengths, you can precisely determine those wavelengths. (You could also try to measure ✓ values for the |m| > 1 maxima, but as |m| increases intensity is reduced, so you may not be able to see the m = ±2 maxima.)
A spectroscope allows precise measurement of these angles. The spectroscope you will be using consists of two cylinders that define the light path: one is a collimator; the other a telescope (Fig. 19a). The collimator has an opening at its far end that only admits light through a vertical slit. The width of the slit is narrow but adjustable. That slit shapes the light beam into a vertical line. Letting the light spread vertically doesn’t degrade the resolution in ✓ because ✓ is an angle in the horizontal plane. Because a line allows more light to hit the detector (in this case, your eye) it is much easier to determine the location of a line than a point. The use of vertical slits in spectral measurements is so common that the observed maxima are called spectral lines.
The telescope part of the spectroscope allows you to scan through angles to find these lines and precisely measure their ✓ angle. The telescope has an adjustable eyepiece, to allow you to focus on the lines, and cross-hairs to help with visual alignment. The angular position of the telescope can be measured with scales situated on either side of the spectrometer. The scales measure degrees down to

10It is amusing to note how often dialogue in Star Trek episodes involves the captain asking for a “multi-spectral analysis” of some anomaly. Analyzing the spectrum of astrophysical objects is common, in fact so common that it would be done automatically, without the captain’s specific request! But, it does provide tech-y sounding, and in this case not incorrect, dialogue.

one arc minute with Vernier markings.
Use of a Vernier scale takes a bit of explanation and some practice. There are some good extended descriptions online (e.g. in Wikipedia), (http://en.wikipedia.org/wiki/Vernier_scale) so here we’ll introduce it with a few examples specific to the scales you will be using. On the spectroscope, you will see a pair of scales that are arranged so that they slide past each other. The outer one has line markings for each half degree, while the inner one has markings corresponding to 0-30 arc minutes. The two scales are used together. Cartoons of two different measurements are shown in Fig. 20 to illustrate the procedure. First you look where the zero mark on the inner scale is located. In the left hand cartoon that is just past 210; in the right hand cartoon it is just past 229.5. Then you look where the lines on the inner and outer scales align most closely. In the left hand cartoon that happens for the 150 mark; on the right side it happens at the 160 mark. These measure the number of arc minutes to add to the values obtained from the first step. So, the measurement on the left side is 210 + 150 = 210 + (15/60) = 210.250, and the measurement on the right is 229.5 + 160 = 229.5 + (16/60) = 229.767. To practice this yourself, figure out the measurement for the photo in the middle. Write your result in your logbook and, when you get to lab, compare it to what other students got.
The uncertainty in ✓ is driven by the one arc minute granularity of the scales, so it is appropriate to
use ✓ =10
/

p12 = 0.30 =0.005. The scales thus provide rather precise angular measures, but it is possible to make mistakes in reading or calculating the values. There are a few things you can do to reduce the chance of such mistakes and their impact. First of all, you could have someone else (e.g. your lab partner) make the same reading (without telling them what you got) and compare. Secondly, the spectroscope has a scale on both sides, where the angles differ by 180; you should read and record both. If, after correcting for the 180 difference, you find that their values differ by more than the 0.005 precision of the scales, then there is an additional source of uncertainty. That could arise from things like warping of the scales, and it would then be the dominant uncertainty on your ✓ measurements. This approach of making multiple, independent measurements of the same quantity is always a good idea to help you validate your results.
It is also a good idea to record your raw readings in degrees and arc minutes, and then calculate the corresponding decimal degree values. This will help you disentangle any calculation errors that may occur. While the calculations in this case are not complicated, and the consequences of a mistake are small, this sort of fastidious data recording is a good habit to develop for your later research work, when both the chances and consequences of mistakes increase.
Finally, be aware that the scale measures an angular position on some arbitrary scale (i.e., the location of 0 is arbitrary). What you want to know in order to determine the wavelength using d sin ✓ = is the angle between maxima. So you need to measure two angles and subtract, just like measuring a length requires two position measurements. You could do that by measuring the angular position of the central maximum, which we can call ✓0, and the angular position of the m = +1 maximum, which we can call ✓+1. Then = d sin (✓+1 ✓0). Similarly, you could measure the angular position of the m = 1 maximum and use = d sin (✓0 ✓1). If everything is perfectly aligned, (✓+1 ✓0)=(✓0 ✓1). If not, then neither value will be correct. You can cancel the effects of any mis-alignment by using both the m = +1 and m = 1 positions, i.e., = d sin (✓+1 ✓1)/2. Since you can’t be certain that the diffraction grating is exactly perpendicular to the light path and the spectroscope’s angular coordinate system, you must use this difference of the two angles. Finally, note that the direction in which the angles increase or decrease on the scale is arbitrary, so you should use the absolute value of the differences

= d sin

✓+1 ✓1

(15)

### 5.1.2 Safety and care of equipment

Be careful not to touch the glass part of the lamp, even when it’s off. Not only might it be hot enough to burn you, but any oil from your fingertips that gets on the glass can absorb enough light energy to cause the glass to overheat and shorten the life of the lamp.
To help you discern the dim spectral lines, it is best to leave the room lights off. There is a desk lamp, but you should use it very sparingly. You can use the small flashlight provided when you need to read the angle scales. Reading the angle by taking a picture of the scale with a phone and then using the phone’s digital zoom can help minimize errors in reading the Vernier. You will notice that there is considerable potential for parallax errors when reading the scales, either by eye or by phone. Think what you might do to minimize associated errors.
Keep in mind that the darkness and crowdedness of the room means you might back into or trip others who are trying to move around the lab (like your TA). In such situations it is a good idea to just move a bit more slowly.
The spectroscope has clamps to hold it in place while you measure angles. If you forget to release the clamps before trying to adjust the angle, you can damage the spectroscope. So, do not force any motion that doesn’t feel smooth.

### 5.2 Getting started and gaining familiarity

Start with the Hydrogen discharge tube. There are two other tubes that contain other elements, which you will use next, but it’s best to get familiar with the measurement on a simple spectrum like that of Hydrogen.
Play around with the spectroscope to make sure you understand how it works: align the telescope and collimator, and adjust the slit and crosshairs.
The grating should be approximately perpendicular to the light path. You can adjust it and lock its table in place. Any misalignment will skew the angles slightly, so as noted above, so you should measure the position of the spectral lines for both m = +1 and m = 1 and use half the difference to reduce the effect of any misalignment.
Look for each of the emission lines. You should see a total of four, although the last one, which is violet, is dim and difficult for some people to see. You can increase the slit width to make the lines easier to see, although you want to balance the need for visibility with the desire for narrow lines that can be measured more precisely. You may see a background of colors in addition to the main bright lines. This background can come either from stray light hitting the diffraction grating or from the ultraviolet light emitted by the hydrogen lamp exciting other atoms to emit. In fact, that is how fluorescent lights work. Ultraviolet emission produced by running a current through the gas in a long tube excites atoms in the white fluorescent material that coats the inside of the tube. That material then emits a large number of different wavelengths that we perceive as white light. You can use the hand held spectroscope (black trapezoidal object) provided to check out the spectrum of the fluorescent lights in the lab’s ceiling.

### 5.3 Measuring the spectrum and extracting Rydberg’s constant

Measure the angles for each of the spectral lines. (Remember to measure the position on both sides to correct for any misalignment of the grating, and to clamp the telescope before making a reading and then unclamp it before moving again.) If you are working with a lab partner, you should both take measurements independently. I suggest that one of you collect a full set of measurements and then the other collect another full set. You can each record readings for the other’s dataset as a cross-check, but it is instructive to independently collect (i.e. align the cross-hairs) and analyze your own dataset. The writing in your logbook should make it clear who collected which data.
Once you have measured the angular positions of each of the emission lines, calculate their wavelengths and determine the uncertainty in the wavelengths. To find the uncertainty you will need to propagate the uncertainties in each of the measured angles, ✓i, to derive the uncertainty in using the standard error propagation approach described in Equation (5).
Then use Equation (14) to extract the Rybderg constant, R. This can be done in several ways, such as averaging all the measurements or fitting them. A fit is usually the best approach because it incorporates the uncertainties in each of the measurements, and the ² of the fit provides a quantitative way to validate the measurements and uncertainties. So, fit your data.
Think about what would be the best functional form to use for the fit. It is not simple to solve Equation (14) for (n), but you can calculate terms that are easy to plot. For example, a plot of y = 1/ versus x =1/2² 1/n² should be a line with a slope equal to R. Remember to propagate the uncertainties properly though! The uncertainty in y =1/ must be derived from the uncertainty in using Equation (5).
If the ² of your fit is too large or too small, it can indicate that your uncertainties are incorrectly estimated or that you made a mistake in calculating. The best way to figure this out is to make multiple measurements and compare them. If different measurements of the same quantity disagree completely then there is a mistake somewhere. (Note that recording the “color” of the lines you observe provides a coarse measurement of their wavelength, which you can use to validate that you have not made a major mistake in calculating from the measured angles). You can also compare your measured values from one set of data to the values from another set. They should agree to within the uncertainties that you have determined. If the disagreements are a bit larger than the uncertainties, you may have underestimated the uncertainties. Increasing the uncertainties on the ’s to make the level of agreement between repeated measurements of them match a 68% confidence level will then make the uncertainty on the fitted R value more appropriately correspond to a 68% confidence level.

### 5.4 Measuring the spectrum of an unknown source

There are two other discharge tubes provided. They contain other elements. Replace the hydrogen tube with either one of these and measure its spectrum. You can remove the tubes by pushing them up and out of the black mounting box. The new ones should then slide in easily. Don’t force it.
Compare your measured spectrum to the spectra given for standard sources in the following pages and determine the composition of the discharge tube. Note that, in some cases, the relative intensity of the different lines can be helpful, so it is wise to record a qualitative measure of that.

### 5.5 Going Beyond

There are several ways that exceptional students could go beyond the basics in this lab. A few ideas are listed below, but I encourage you to use your own creativity.
- Can you think of a way to quantitatively record the relative intensity of the emission lines?
- Can you use your measured value of the Rydberg constant, and Bohr’s energy level calculation, to extract an upper or lower bound on the proton mass?
- Now that you understand how to use the spectroscope, can you use it to measure the spectrum of something else?

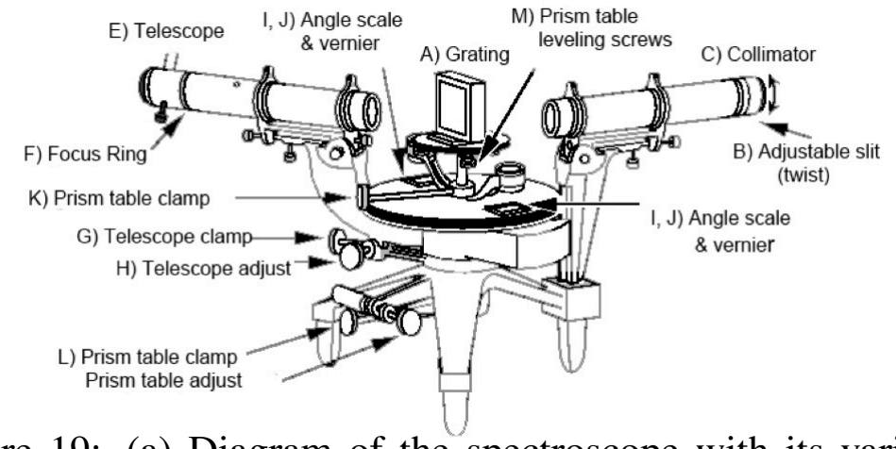
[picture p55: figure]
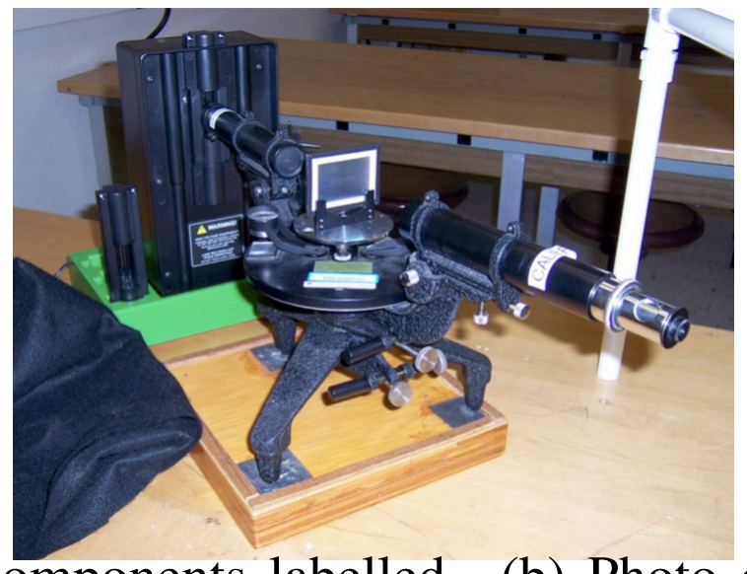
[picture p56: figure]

Figure 19: (a) Diagram of the spectroscope with its various components labelled. (b) Photo of the spectroscope. The light source is contained in the square black device behind it.

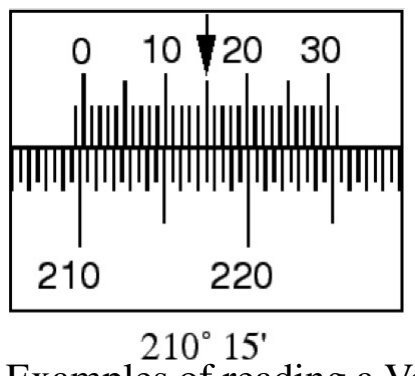
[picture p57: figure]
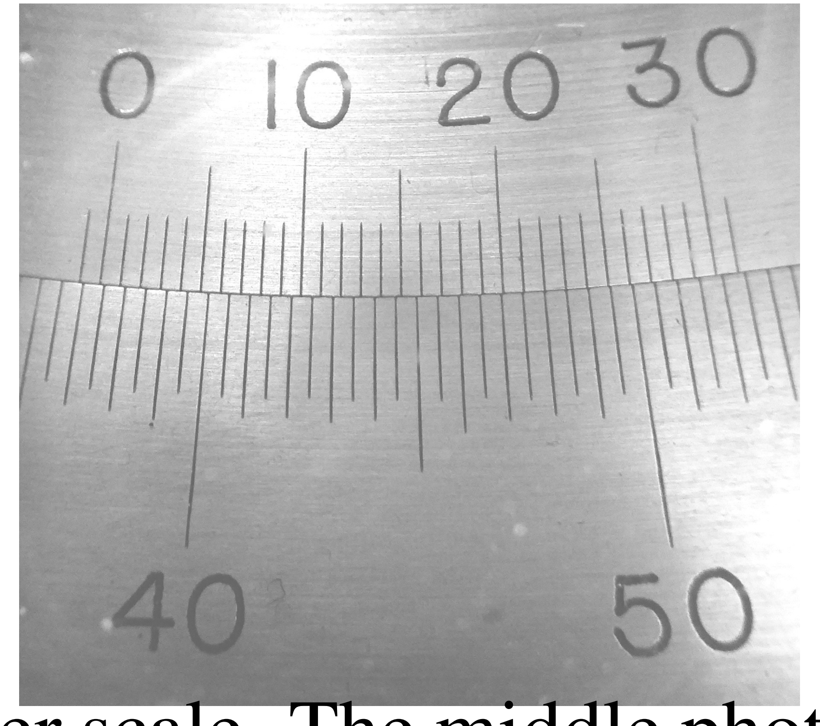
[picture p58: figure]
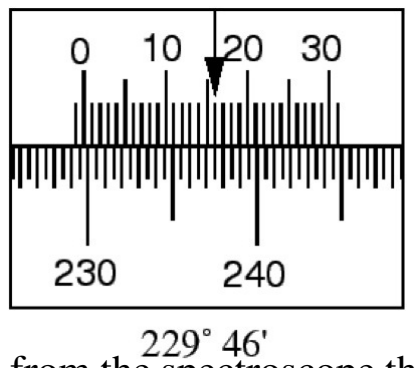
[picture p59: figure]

Figure 20: Examples of reading a Vernier scale. The middle photo is from the spectroscope that you will use. The left and right cartoons are discussed in the text to illustrate how to read the scale; the arrows in the cartoon show where the lines on the inner and outer scale are most closely aligned.

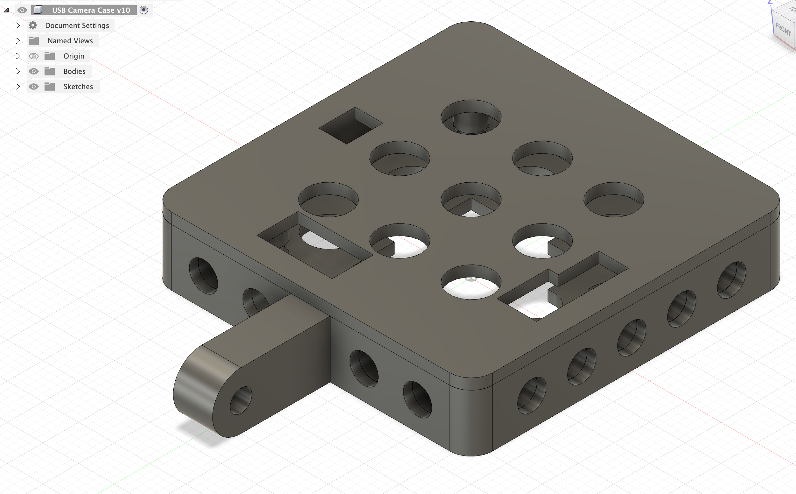
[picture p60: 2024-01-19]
3D-Prints/General Use/USB Camera Case.png

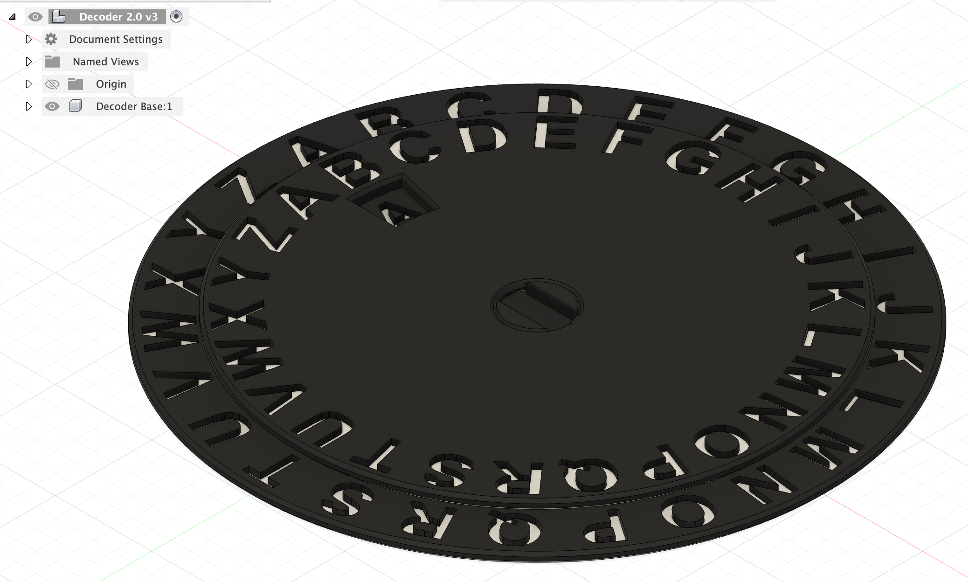
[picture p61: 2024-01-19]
3D-Prints/Broida Welcome Event/Decoder.png

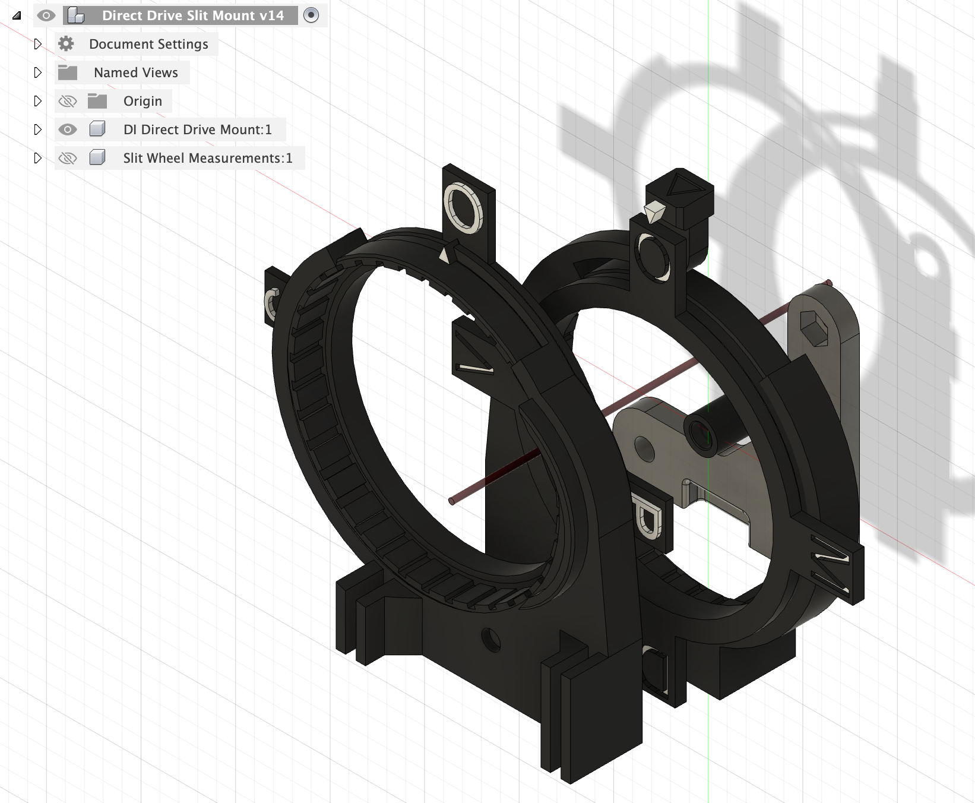
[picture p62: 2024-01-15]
3D-Prints/Diffrac3D/Direct Drive Slit Mount.png

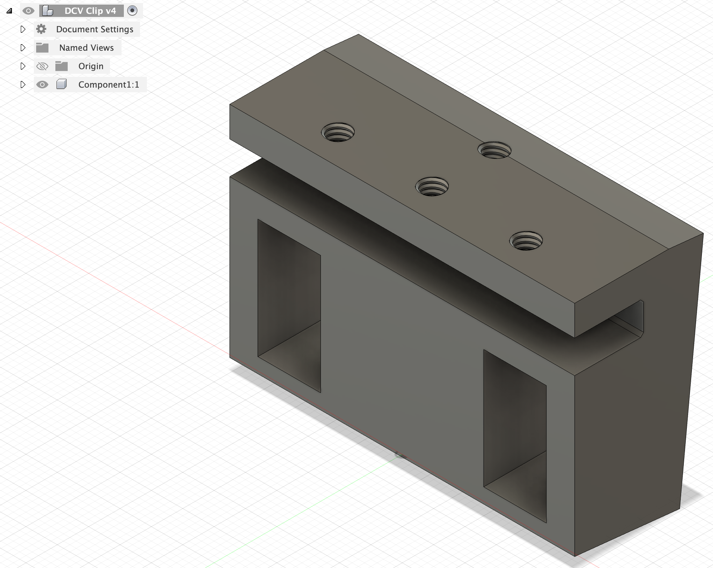
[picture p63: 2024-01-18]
3D-Prints/Franck3D/DCV Clip.png

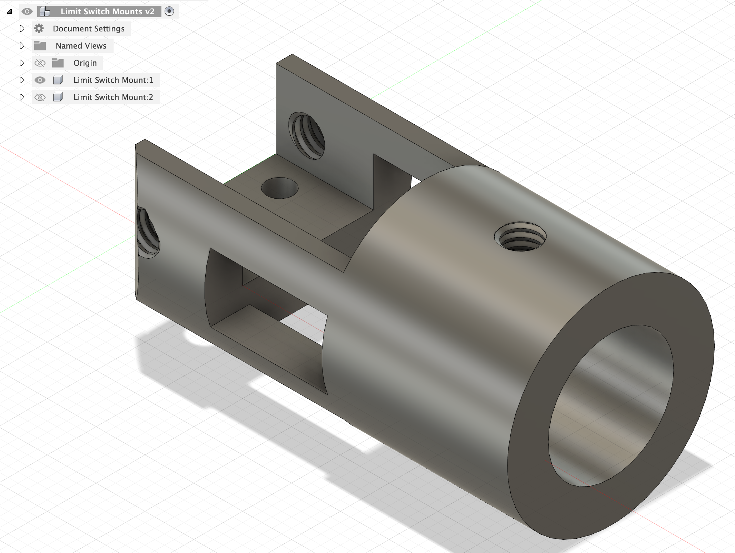
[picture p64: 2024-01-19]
3D-Prints/Atomic3D/Limit Switch Mounts.png

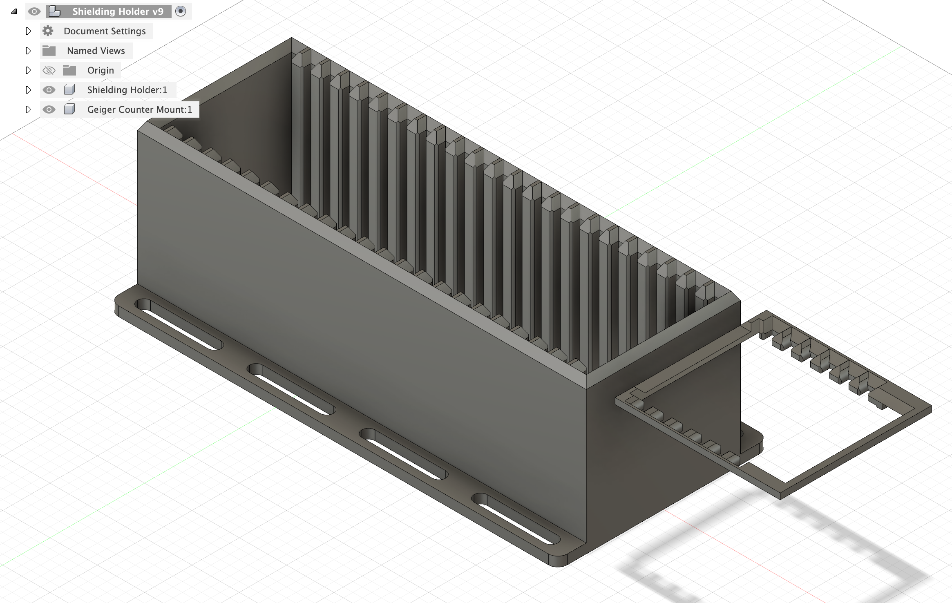
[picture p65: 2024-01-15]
3D-Prints/Gamma3D/Shielding Holder.png

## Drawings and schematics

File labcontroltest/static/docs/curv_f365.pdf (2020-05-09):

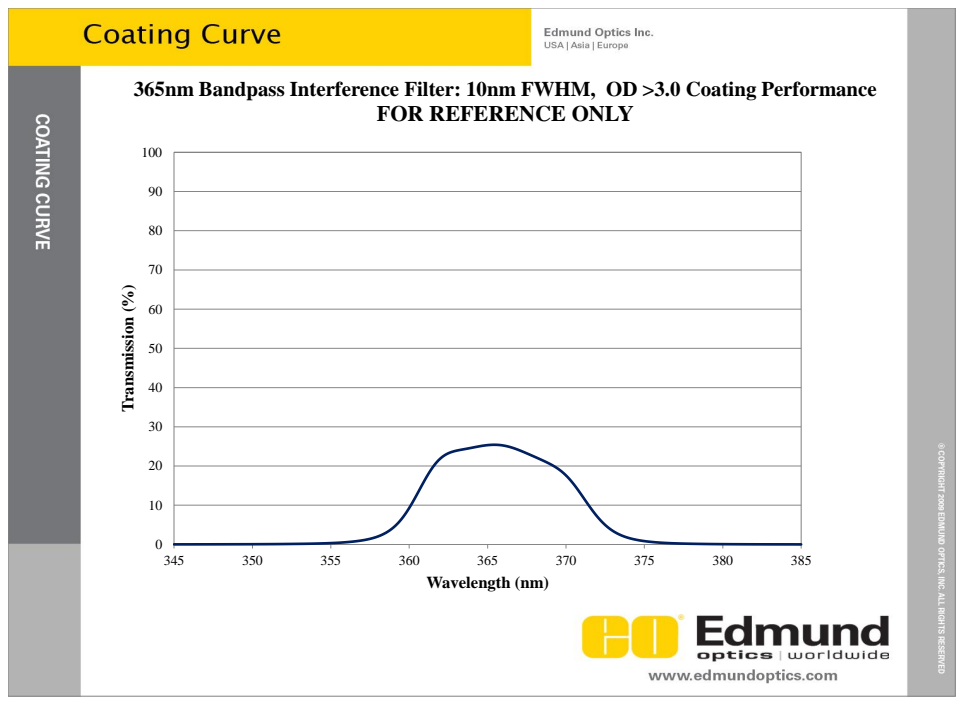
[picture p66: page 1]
Transmission (%); Wavelength (nm)

365nm Bandpass Interference Filter: 10nm FWHM, OD >3.0 Coating Performance

FOR REFERENCE ONLY

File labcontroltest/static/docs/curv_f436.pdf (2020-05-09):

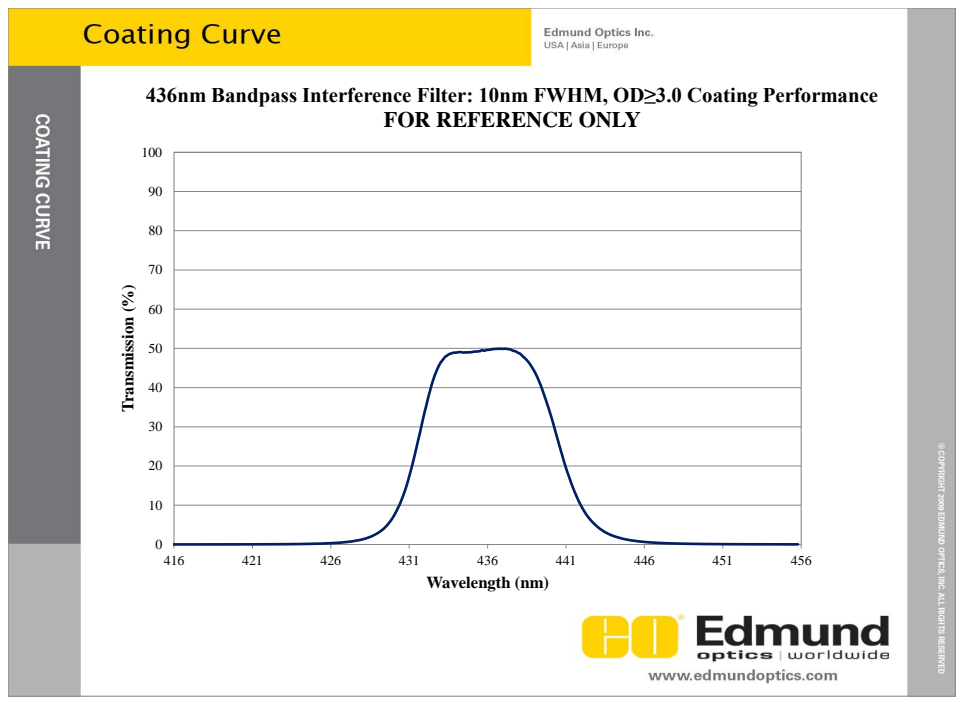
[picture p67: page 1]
Transmission (%); Wavelength (nm)

436nm Bandpass Interference Filter: 10nm FWHM, OD≥3.0 Coating Performance

FOR REFERENCE ONLY

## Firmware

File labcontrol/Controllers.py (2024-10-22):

import time
import tplink_smarthome as tp
import dlipower
import RPistepper as stp
from adafruit_motorkit import MotorKit
from adafruit_motor import stepper
import RPi.GPIO as gpio
import os
import subprocess
import busio
import board
import signal
from adafruit_bus_device.i2c_device import I2CDevice
import pigpio
import sys
from warnings import warn


pi = pigpio.pi()
gpio.setmode(gpio.BCM)

class BaseController(object):

    def cmd_handler(self, cmd, params, queue, device_name): # this should recieve a command, and a queue where it sends its response
        
        # Aquires lock
        self.experiment.locks[self.name].acquire()

        # Make the parser name, it should follow the naming convention <cmd>_parser. If there is no parser return None.
        parser = getattr(self, cmd+"_parser", None)

        # If parser exists, use it to parse the params.
        if parser is not None:
            params = parser(params)
        # If there is no parser print this statement for user.
        else:
            print("No Parser Found. Will just pass params to command.")

        # Now get the command method. If there isn't a method, it will log the erroneous cmd.
        try:
            method = getattr(self, cmd)
        except:
            print(f"{self.__class__.__name__} does not have <{cmd}> cmd")

        if callable(method):
            response = method(params)

            # returns response
            queue.put([response, device_name])

        # Releases lock
        self.experiment.locks[self.name].release()

    def cleanup(self):
        pass

    def reset(self):
        pass

    def getState(self):
        return self.state

    def setState(self, state):
        self.state = state



class PDUOutlet(dlipower.PowerSwitch, BaseController):
    def __init__(self, name, hostname, userid, password, timeout=None, outlets=[1,2,3,4,5,6,7,8], outletMap={}):
        # self, userid=None, password=None, hostname=None, timeout=None, cycletime=None, retries=None, use_https=False
        super().__init__(hostname=hostname, userid=userid, password=password, timeout=timeout)
        self.name = name
        self.device_type = "controller"
        self.experiment = None
        self.state = {1:"Off", 2:"Off", 3:"Off", 4:"Off", 5:"Off", 6:"Off", 7:"Off", 8:"Off" }
        self.outlets = outlets
        self.outletMap = outletMap

    def on(self, outletNumber):
        super().on(outletNumber)
        self.state[outletNumber] = "On"

    def off(self, outletNumber):
        super().off(outletNumber)
        self.state[outletNumber] = "Off"

    def on_parser(self, params):
        if len(params) != 1:
            raise ArgumentNumberError(len(params), 1, "on")
        try:
            outlet = int(params[0])
        except ValueError:
            outlet_name = params[0]
            if outlet_name not in self.outletMap:
                raise ArgumentError(outlet_name, self.outletMap, self.name, "On")
            outlet = self.outletMap[outlet_name]

        if outlet not in self.outlets:
            raise ArgumentError(self.name, "On", "Outlet "+ params[0], allowed="Outlets " + str(self.outlets))
        return outlet

    def off_parser(self, params):
        if len(params) != 1:
            raise ArgumentNumberError(len(params), 1, "off")
        try:
            outlet = int(params[0])
        except ValueError:
            outlet_name = params[0]
            if outlet_name not in self.outletMap:
                raise ArgumentError(outlet_name, self.outletMap, self.name, "Off")
            outlet = self.outletMap[outlet_name]

        if outlet not in self.outlets:
            raise ArgumentError(self.name, "Off", "Outlet "+ params[0], allowed="Outlets " + str(self.outlets))
        return outlet

    def reset(self):
        for outlet in self.outlets:
            self.off(outlet)


class Plug(tp.TPLinkSmartDevice, BaseController):
    def __init__(self, name, host, port=9999, timeout=10, connect=True):
        print(host, port, timeout, connect)
        super().__init__(host=host, port=port, connect=connect)
        self.name = name
        self.device_type = "controller"
        self.experiment = None
        self.state = {"relayState": "OFF"}

    def setRelay(self,newRelay):
        print(newRelay)
        if newRelay=="OFF":
            super().send({'system': {'set_relay_state': {'state': 0}}})
        elif newRelay=="ON":
            super().send({'system': {'set_relay_state': {'state': 1}}})
        self.state["relayState"] = newRelay

    def setRelay_parser(self, params):
        if len(params) != 1:
            raise ArgumentNumberError(len(params), 1, "setRelay")
        return params[0]

    def cleanup(self):
        super().close()

    def reset(self):
        super().send({'system': {'set_relay_state': {'state': 0}}})
        super().close()


class StepperSimple(stp.Motor, BaseController):

    def __init__(self, name, pins, delay=0.02, refPoints={}):
        super().__init__(pins, delay)
        self.name = name
        self.device_type = "controller"
        self.refPoints = refPoints
        self.currentPosition = 0
        self.experiment = None
        self.state = {"position": self.currentPosition}

    def move(self, steps):
        print(steps)
        super().move(steps)
        super().release()
        self.currentPosition+=steps
        self.state["position"] = self.currentPosition
        self.device.release()

    def move_parser(self, params):
        if len(params) != 1:
            raise ArgumentNumberError(len(params), 1, "move")
        return int(params[0])

    def goto(self, position):
        print(position)
        endPoint=self.refPoints[position]
        self.move(endPoint-self.currentPosition)

    def goto_parser(self, params):
        if len(params) != 1:
            raise ArgumentNumberError(len(params), 1, "goto")
        return params[0]

    def cleanup(self):
        super().cleanup()

    def reset(self):
        super().reset()


class DCMotorI2C(MotorKit, BaseController):

    def __init__(self, name, terminal):
        if terminal > 4:
            self.address=0x61
        else:
            self.address=0x60
        super().__init__(address=self.address)
        self.name = name
        self.device_type = "controller"
        self.experiment = None

        self.terminal_options = {1: super().motor1, 2: super().motor2, 3:super().motor3, 4:super().motor4,
            5: super().motor1, 6:super().motor2, 7:super().motor3, 8:super().motor4}
        self.device = self.terminal_options[terminal]
        self.currentPosition = 0
        self.state = {"position": self.currentPosition}

    def setup(self, style):
        pass

    def reset(self):
        pass

    def throttle(self, speed):
        self.device.throttle = speed

    def throttle_parser(self, params):
        if len(params) != 1:
            raise ArgumentNumberError(len(params), 1, "move")
        print("Throttle is set to: {0}".format(params[0]))
        return float(params[0])

# Initialise the first hat on the default address
# lowerBoard = MotorKit()
# Initialise the second hat on a different address
# upperBoard = MotorKit(address=0x61)

class StepperI2C(MotorKit, BaseController):

    def __init__(self, name, terminal, bounds, delay=0.02, refPoints={}, style="SINGLE", microsteps=8, limitSwitches=[], homeSwitch=None, degPerStep=1.8, gearRatio=1):
        if terminal > 2:
            self.address=0x61
        else:
            self.address=0x60
        super().__init__(address=self.address, steppers_microsteps=microsteps)
        self.name = name
        self.device_type = "controller"
        self.experiment = None

        self.terminal_options = {1: super().stepper1, 2: super().stepper2, 3:super().stepper1, 4:super().stepper2}
        self.refPoints = refPoints
        self.currentPosition = 0
        self.device = self.terminal_options[terminal]
        self.delay = delay
        self.lowerBound = bounds[0]
        self.upperBound = bounds[1]
        self.styles = {
            "SINGLE": stepper.SINGLE,
            "DOUBLE": stepper.DOUBLE,
            "MICROSTEP": stepper.MICROSTEP,
            "INTERLEAVE": stepper.INTERLEAVE
        }
        self.style = self.styles[style]

        self.state = {"position": self.currentPosition}
        self.limitSwitches = limitSwitches
        self.homeSwitch = homeSwitch
        self.homing = False
        self.degPerStep = degPerStep
        self.gearRatio = gearRatio
        self.device.release()

    def setup(self, style):
        pass

    def move(self, steps):
        print(steps)
        if steps >= 0:
            direction = stepper.BACKWARD
        else:
            direction = stepper.FORWARD
        if self.currentPosition+steps <self.lowerBound and steps < 0:
            steps = self.lowerBound-self.currentPosition
        elif self.currentPosition+steps >self.upperBound and steps > 0:
            steps = self.upperBound-self.currentPosition

        for i in range(abs(steps)):

            if len(self.limitSwitches) != 0:
                for switch in self.limitSwitches:
                    status = switch.getStatus(1)
                    if status == gpio.HIGH:
                        response = switch.switchAction(self, steps-i)
                        if response is None:
                            return "{0}/{1}/{2}".format(self.name, "position", "limit")
                        else:
                            return response

            if self.homing:
                homeStatus = self.homeSwitch.getStatus(1)
                if homeStatus == gpio.HIGH:
                    return True

            self.device.onestep(style=self.style, direction=direction)
            time.sleep(self.delay)

        self.currentPosition+=steps
        self.state["position"] = self.currentPosition
        self.device.release()
        if self.currentPosition == self.upperBound or self.currentPosition == self.lowerBound:
            return "{0}/{1}/{2}".format(self.name, "position", "limit")
        else:
            return "{0}/{1}/{2}".format(self.name, "position", self.currentPosition)

    def move_parser(self, params):
        if len(params) != 1:
            raise ArgumentNumberError(len(params), 1, "move")
        return int(params[0])

    def adminMove(self, steps):
        if steps >= 0:
            direction = stepper.BACKWARD
        else:
            direction = stepper.FORWARD
        if self.currentPosition+steps <self.lowerBound and steps < 0:
            steps = self.lowerBound-self.currentPosition
        elif self.currentPosition+steps >self.upperBound and steps > 0:
            steps = self.upperBound-self.currentPosition
        for i in range(abs(steps)):
            self.device.onestep(style=self.style, direction=direction)
            time.sleep(self.delay)
        self.currentPosition+=steps
        self.state["position"] = self.currentPosition
        self.device.release()

    def goto(self, position):
        print(position)
        endPoint=self.refPoints[position]
        response = self.move(endPoint-self.currentPosition)
        return response

    def admingoto(self, position):
        print(position)
        endPoint=self.refPoints[position]
        response = self.adminMove(endPoint-self.currentPosition)
        return response

    def goto_parser(self, params):
        if len(params) != 1:
            raise ArgumentNumberError(len(params), 1, "goto")
        return params[0]
    
    def admingoto_parser(self, params):
        if len(params) != 1:
            raise ArgumentNumberError(len(params), 1, "admingoto")
        return params[0]

    def degMove_parser(self, params):
        try:
            steps = float(params[0])
        except ValueError:
            raise ArgumentError(self.name, "degMove", params)
        return steps
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

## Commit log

2020-04-23 #created all needed devices in pEcontroller
2020-05-01 added filterwheel
2020-05-01 update filterwheel to cutout
2020-05-26 added all the power switches
2020-05-30 mounting skeleton from webflow
2020-05-31 encoded Power Switches
2020-06-01 final addressing of motors
2020-06-02 added print line alerting of initial running of experiment
2020-06-02 got plugs and motors working
2020-06-09 Added Camera to controller and testsite for LC
2020-06-16 changed StepperI2C default delay to 0.2 to reduce probability of dropped steps
2020-06-16 added camera button listeners
2020-06-18 added hangup to beforeunload; made divs toggle with camera selection
2020-06-25 Fixed Camera values
2020-07-03 various efforts to fix the power buttons and troubleshoot the motors
2020-07-06 nothing really - troubleshooting motor/camera conflict
2020-07-07 corrected BCM pin designation for the camera hat
2020-07-07 added controller code to mimic Arducam init code setting up (BOARD) pins 15, 16, 21, 22
2020-07-08 Changed camera bus to i2c-11 instead of i2c-1
2020-07-08 Added info on pullup resistors.
2020-07-10 bringing all the devices back into the experiment
2020-07-10 enabled specificastion of step type for motors
2020-07-21 Fixed motor step style
2020-07-21 moved filament controls to side panels, added links to Tube images
2020-07-22 Added Ambient LED by SingleGPIO pin 29
2020-07-22 Activated Camera
2020-07-22 Switch to correct number of pin
2020-07-22 corrected camera channels
2020-07-30 updated for new gearing system on carousel
2020-08-01 added laser toggle and corrected imagemaps
2020-08-01 assigned cameras correctly
2020-08-02 added laser toggle
2020-08-02 added laser event listener
2020-08-02 corrected cameras and made laserSwitch visible in dark mode
2020-08-02 Updated controllers to stage is motor 4
2020-08-02 First pass slit calibration
2020-08-02 corrected sing of stage steps
2020-08-02 removed laserSwitch imagemap
2020-08-02 make modal active waiting for datachannel so that first screen need not be camera a
2020-08-02 finalized motor delay times and set preliminary bounds in all controllers
2020-08-03 moved camera buttons to top of central div
2020-08-03 moved camera selector buttons to lowest row of PageHead
2020-08-03 Adding some camera changes
2020-08-04 Updated Carousel Motor Parameters
    Double steps, changed delay, changed reference points
2020-08-04 Carousel Motor Argument
2020-08-04 removed laser added console log for message handler
2020-08-04 print statesments for testing
2020-08-04 print statement for troubleshooting
2020-08-05 Huge delay plus print statements
2020-08-06 Changed motor sign and added 0 position update
2020-08-06 Print testing
2020-08-06 More print statements
2020-08-10 Added back the closeUp of the tube that displays in Tube view
2020-08-10 motor fix
2020-08-10 Updated diffrac2settings to calibrate the slits
2020-08-10 corrected font case in line 5 of photo2Settings
2020-08-14 Franck 1&2 Variac Motor fixed with degMove
2020-08-18 Updated the calibration for the slits
2020-08-20 Updating code to release motor when starting the controller.
2020-08-25 Used update camera function to change settings so they would be tracked.
2020-08-25 Added reset function to camera upon exit
2020-10-09 moved motor controls above live feed
2020-10-09 tweaked video wrapper height in hopes of revealing camera controls beneath
2020-10-09 returned video height to 100, tried getting laser and schematic side by side
2020-10-09 tweaked laser clicknote
2020-10-09 added space between timer warning and laser/motor controls
2020-10-09 added horizontal rule between timer and laser/motor controls
2020-10-09 tweaked size of motor controls
2020-10-09 tried moving camera buttons above motor controls
2020-10-09 enlarged motor controls
2020-10-09 tried adding a <br> to nudge the laser control lower
2020-10-09 resized motor controls
2020-10-09 Revert "resized motor controls"
    This reverts commit 6a95ef0bca79ea1733b530e630ed48c40cd121ac.
2020-10-09 Revert "tried adding a <br> to nudge the laser control lower"
    This reverts commit 779ec7c92caaea11705a843752ab61caff351fba.
2020-10-10 changes to incorporate ND filter wheel
2020-10-21 removed background on density filter cropped
2020-10-28 Getting the motor added.
2020-10-30 fixed filter and moved to right side
2020-11-05 Updated ND Filter Wheel
2020-11-05 fixed desityfilterwheelscalledcropped so filter is in correct position
2020-11-17 Centered Denisty Filter cropped
2020-12-28 Removed Camera Feeed Blocking
2021-01-26 Changed Single Slit motor to Microsteps
2021-01-26 SS Calibration
2021-02-02 Slit Calibrations
2021-02-02 DI 1 calibration
2021-02-17 set camera control to visible
2021-02-17 changed id in javascript for camera modal
2021-02-17 added camera div id
2021-02-22 Added camera modal
2021-02-22 camera modal
2021-02-24 changed to current stage steps
2021-02-24 changed curr stage step to stage step
2021-03-07 deleted print statements
2021-03-11 Started GR1 Calibration
2021-03-11 GR1 stage
2021-03-15 Change PWM Frequency and motor delay
2021-03-16 - Lower Stage Delay - Set Actuator Times - Made main.js send absorber config
2021-03-16 Removed lens of params place arguemnt
2021-03-16 Updated __transfer function to use PWMChannel instead of motor throttle
2021-04-02 Fixed some gammacontroller things + enable pin
2021-04-02 deleted sliders and moved over camera controls modal
2021-04-02 commented out cameraControl in JS
2021-04-04 removed filament controls from tube view
2021-04-04 more white space (for tube view this time)
2021-04-05 Used wrong gname and selecting the correct cameras.
2021-04-05 Added ND Filter info
2021-04-05 camera settings reset to default
2021-04-14 camera settings updated
2021-04-14 stageTerminal -> stagePins
2021-04-14 Made stage negative
2021-04-20 added sys import for stop command of motor crash
2021-04-20 Programmed cut off
2021-04-20 Fixed typo with PUD resistor
2021-04-26 Testing holder print functino
2021-04-27 Fixed slot delation
2021-04-28 Printing out motion
2021-04-28 printing locations
2021-04-28 More print statments
2021-04-28 Printing Moves
2021-04-28 More print statement. Nust be in buildgroups
2021-04-28 Print IGROUPS
2021-04-30 update Eyepiece camera settings
2021-04-30 Added Title to Density Filters
2021-05-03 Calibrated Gamma 2
2021-05-04 Added messenger socket path
2021-05-05 Threaded messenger attempt
2021-05-07 Changed delay for arm motor
2021-05-07 Updated to work with new motor system
2021-05-07 Added messenger socket. Changed direction of motor
2021-05-08 Franck Calibration
2021-05-10 GR1 Calibration
2021-05-10 GR 2 Calibration
2021-05-15 Adding new way to show stage modal so setcart stays
2021-05-15 Fixed type for stageModal
2021-05-15 Added response for goto command on stepper ii2c
2021-05-17 Added sixth slot
2021-05-17 GR2 Calibration
2021-05-21 Lowered stage stepper delay by 1/4
2021-05-21 Lowered stage delay by less
2021-05-21 Set stage delay 0.004 difrac1
2021-05-21 Allowing for stage terminal selection
2021-05-26 calibrated gamma 1
2021-05-27 Updated the framerate.
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2022-04-15 Fixed response printer. Missing self argument
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2023-10-05 fixed photo filter wheel logic
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2023-12-22 gamma threading fix
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2024-01-15 Started 3D Printing Repository
    Created DI Directory
    [Camera Cradle Version 1 v4.f3d, Cart Mount v2.f3d, DI Direct Drive Motor Junction.stl, DI Direct Drive Motor Mount 3.0.stl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]
2024-01-15 Updated 3D Printing Repository
    Finished PE, started Gamma
    [Double NEMA 17 Motor Mount v7.f3d, GR Concealed Bracket.stl, GR Flat Guard Long.stl, GR Geiger Counter Faceplate.stl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]
2024-01-18 3D Printing Repo Update
    Added Franck Hertz and Gamma Radiation files
    [Absorber Mounts Version 2 v11.f3d, DCV Clip v5.f3d, FH DCV Clip.stl, FH Idler Bearing.stl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]
2024-01-19 3D Printing Repository Update
    Finished 3D Printing Repo
    [1_4 Rod Foot v3.f3d, 1_4_ Rod Foot v2.stl, 20BL Top v5.f3d, AS Camera Mount.stl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]
2024-03-15 Adding Carousel arm files via upload
    [Carousel Arm Encoded Motor.3mf, Carousel Arm Encoded Motor.f3d, Carousel Arm for Frankenmotor.3mf, Carousel Arm for Frankenmotor.f3d]
2024-03-15 Rename 3D-Prints/Atomic3D/Carousel Arm Encoded Motor.f3d to 3D-Prints/Atomic3D/Carousel Arms/Carousel Arm Encoded Motor.f3d
    [Carousel Arm Encoded Motor.f3d]
2024-03-15 Rename 3D-Prints/Atomic3D/Carousel Arm Encoded Motor.3mf to 3D-Prints/Atomic3D/Carousel Arms/Carousel Arm Encoded Motor.3mf
    [Carousel Arm Encoded Motor.3mf]
2024-03-15 Rename 3D-Prints/Atomic3D/Carousel Arm for Frankenmotor.3mf to 3D-Prints/Atomic3D/Carousel Arms/Carousel Arm for Frankenmotor.3mf
    [Carousel Arm for Frankenmotor.3mf]
2024-03-15 Rename 3D-Prints/Atomic3D/Carousel Arm for Frankenmotor.f3d to 3D-Prints/Atomic3D/Carousel Arms/Carousel Arm for Frankenmotor.f3d
    [Carousel Arm for Frankenmotor.f3d]
2024-10-21 added PCB designs and documentation
    [BOM_RemlaHAT_Remla Atomic HAT PCB_2024-10-21.csv, PickAndPlace_Remla Atomic HAT PCB_2024-10-21.csv]
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
